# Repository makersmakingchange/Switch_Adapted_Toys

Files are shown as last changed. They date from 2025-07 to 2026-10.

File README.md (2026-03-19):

# Switch Adapted Toys
Welcome to the Maker's Making Change resources for Switch Adapted Toys.

This repository is a collection of guides, files, and tools to help individuals and organizations modify toys for use with assistive switches. These adaptations make play more inclusive for children and adults with limited mobility, giving them the power to activate toys with the press of a button—on their own terms.

## What You'll Find Here
 - How-To Guides: - Step-by-step instructions for adapting toys with simple tools and materials and an easy-to-use template for writing toy instructions
 - Educational Resources: Information on how to switch adapt a new toy
 - Equipment lists: Complete list of adapted toys and the tools and components needed to adapt them
 <!-- - Workshop Materials: Handouts and presentation slides for toy hackathons and build nights -->

<!--
## Who This Is For
 - Makers and volunteers interested in assistive technology
 - Therapists and educators supporting play-based learning
 - Families looking to adapt toys at home
 - Nonprofits and schools running toy adaptation workshops
-->

## How To Find a Toy
Toys have been organized by type into separate folders inside the "Toy_Instructions" folder. We have organized the toys this way to help make it easier to find a suitable substitution if you are unable to get the toy someone has requested directly.

You can search for a specific toy by typing in the search field on the repository.

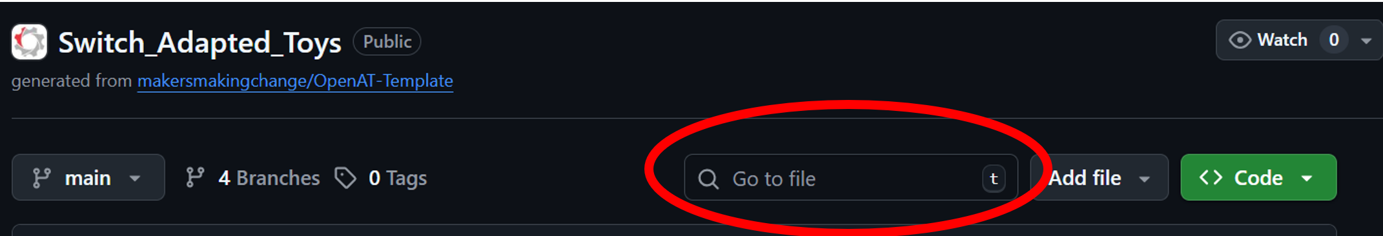
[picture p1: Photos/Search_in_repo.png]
Screenshot of the top of the GitHub repository with the search field circled in red.


The search is very broad, and does not rely on exact  matching between the files/folder you're looking for and what you type. For example, if you type "Rachel", the search will find the Switch Adapted Ms. Rachel Speak and Sing Doll, but also any instances where those letters appear in that order, regardless of what charaters are between them.

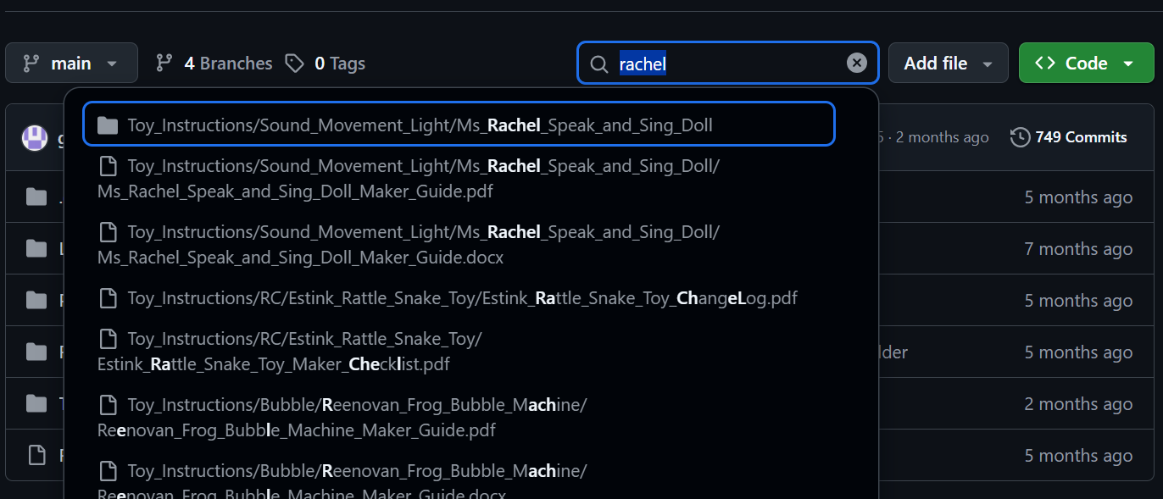
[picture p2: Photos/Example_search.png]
Screenshot of the search results when someone types "Rachel" into the search field.


## Accessing Files

Once you have found the files you need, you can download them from GitHub. You can download individual files by clicking on the down arrow on the page. 

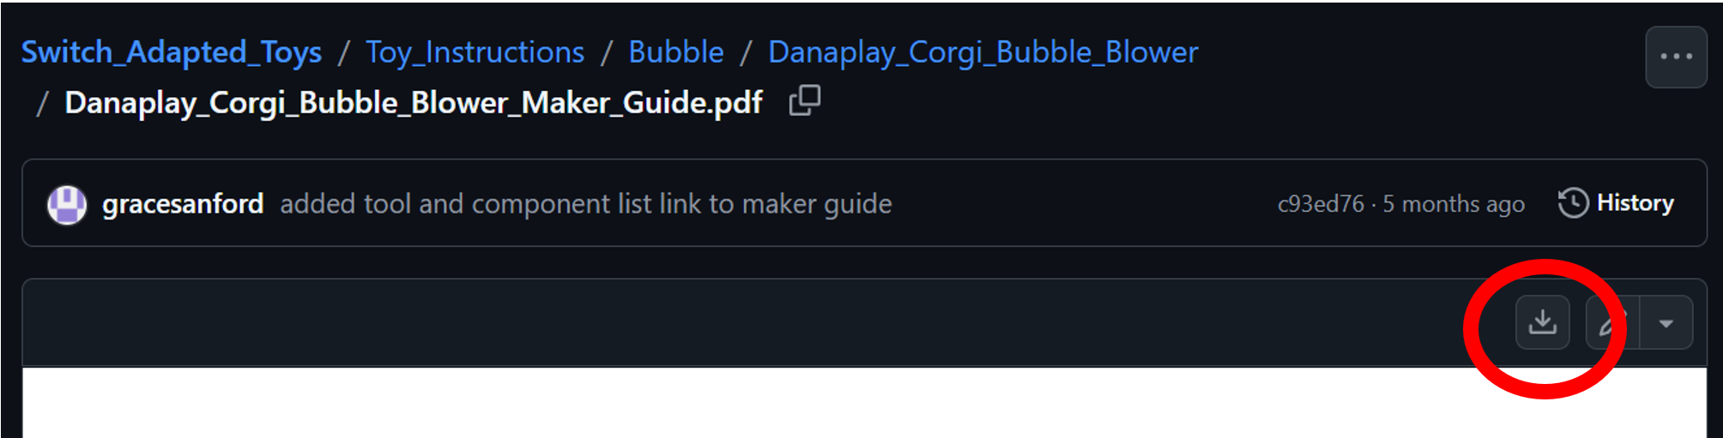
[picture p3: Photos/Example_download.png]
Screenshot highlighting the download button on GitHub.


You will need to download documents (PDFs or Word documents) to be able to access any hyperlinks in those documents.

Some document types, such as Word documents, do not display on the GitHub webpage, and you will have to download them to view. Clicking the "View raw" button will display the files on your web browser (if possible), or download them to your computer.

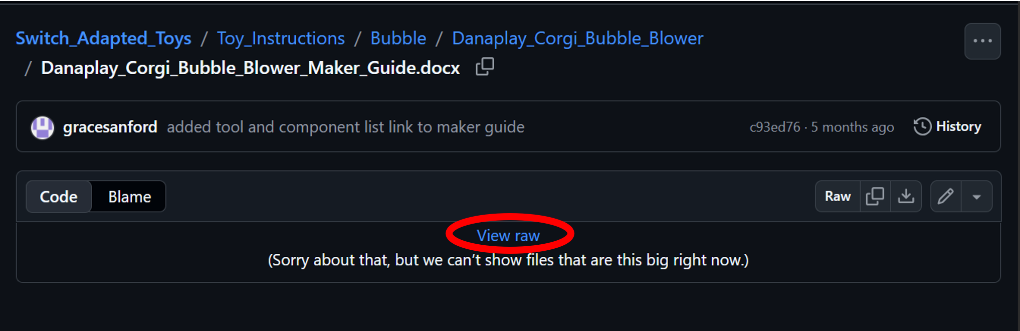
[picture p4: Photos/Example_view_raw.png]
Screenshot highlighting the View raw option for a file type that doesn't preview on GitHub.


## Get Involved
This repository is open source and community-driven. Feel free to open issues, suggest improvements, or submit pull requests! Whether you're documenting your own process or translating guides into another language, your contributions help make inclusive play more accessible for everyone.

## License
All content is shared under the [Creative Commons Attribution-ShareAlike 4.0 License (CC BY-SA 4.0)](https://creativecommons.org/licenses/by-sa/4.0/), unless otherwise noted.

<!-- ABOUT MMC START -->
## About Makers Making Change
[Makers Making Change Logo](https://www.makersmakingchange.com/)

Makers Making Change is a program of [Neil Squire](https://www.neilsquire.ca/), a Canadian non-profit that uses technology, knowledge, and passion to empower people with disabilities.

Makers Making Change leverages the capacity of community based Makers, Disability Professionals and Volunteers to develop and deliver affordable Open Source Assistive Technologies.

 - Website: [www.MakersMakingChange.com](https://www.makersmakingchange.com/)
 - GitHub: [makersmakingchange](https://github.com/makersmakingchange)
 - Bluesky: [@makersmakingchange.bsky.social](https://bsky.app/profile/makersmakingchange.bsky.social)
 - Instagram: [@makersmakingchange](https://www.instagram.com/makersmakingchange)
 - Facebook: [makersmakechange](https://www.facebook.com/makersmakechange)
 - LinkedIn: [Neil Squire Society](https://www.linkedin.com/company/neil-squire-society/)
 - Thingiverse: [makersmakingchange](https://www.thingiverse.com/makersmakingchange/about)
 - Printables: [MakersMakingChange](https://www.printables.com/@MakersMakingChange)

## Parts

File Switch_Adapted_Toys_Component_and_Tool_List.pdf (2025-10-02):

V1.0 | September 2025

## Switch Adapted Toys COMPONENT AND TOOL LIST

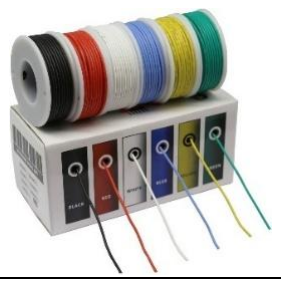
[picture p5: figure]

©2025 Neil Squire Society.

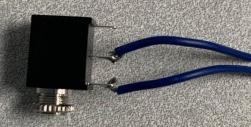
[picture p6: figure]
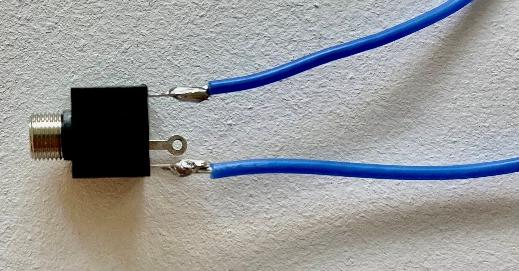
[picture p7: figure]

This work is licensed under the CC BY SA 4.0 License: http://creativecommons.org/licenses/by-sa/4.0
Files available at makersmakingchange/Switch_Adapted_Toys: Resources and instructions for switch adapting toys (https://github.com/makersmakingchange/Switch_Adapted_Toys) Page 1 of 7

This is a list of commonly used components and tools that are used to switch adapt toys. Most items on this list can be purchased from different manufacturers for various prices. The tools are widely used and can be purchased from most local hardware stores. Note that not every tool and component listed is needed to adapt each toy, refer to the first page of the toy’s Maker Guide for more information.

## Components

Device Type | Component | Purchase Link | Notes
| 3.5 mm Rectangular Mono Jack | DigiKey Link (https://www.digikey.ca/en/products/detail/cui-inc/MJ-3502/281321) | Most used Mono Jack. Solder wires onto the two tabs closest to the cable input.
| 3.5 mm Square Mono Jack | DigiKey Link (https://www.digikey.ca/en/products/detail/schurter-inc/4832-2211/2646631) | Solder wires onto the two tabs directly across from each other.
| 22 AWG Wire | Amazon Link (https://a.co/d/4Lc9GPb) | Any 22 AWG silicone wire will work.

Mono Jack

## Switch Adapted Toys COMPONENT AND TOOL LIST

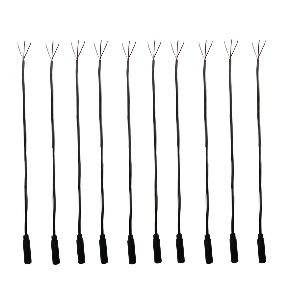
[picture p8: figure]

©2025 Neil Squire Society.

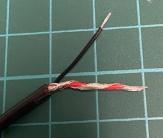
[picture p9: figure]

Files available at makersmakingchange/Switch_Adapted_Toys: Resources and instructions for switch adapting toys (https://github.com/makersmakingchange/Switch_Adapted_Toys) Page 2 of 7

Cables

3.5 mm F/Bare Mono Cable (1 ft) | Amazon Link (https://www.amazon.ca/dp/B082VW97TT?ref=fed_asin_title) | 10 / $20.22.
3.5 mm F/Bare Stereo Cable (1ft) | Amazon Link (https://www.amazon.ca/dp/B0F3791KNY?ref=fed_asin_title&th=1) | To use as a mono cable: Fully strip the insulation off the white wire and 0.5 cm from the red and black wires. Wrap the exposed wire around the red cable. 10 / $10.99
Flex PCB | Request from MMC (https://www.makersmakingchange.com/product/battery-interrupter-flex-pcb/01tJR000000694IYAQ) | -
3.5 mm Mono Jack Flat Rectangular | Digikey Link (https://www.digikey.ca/en/products/detail/cui-devices/SJ1-3513/738683) | Flex PCB is soldered onto the mono jack.

Battery
Interrupter

## Switch Adapted Toys COMPONENT AND TOOL LIST

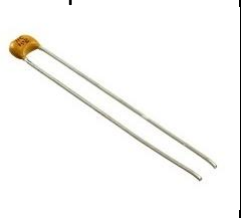
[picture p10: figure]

©2025 Neil Squire Society.

Files available at makersmakingchange/Switch_Adapted_Toys: Resources and instructions for switch adapting toys (https://github.com/makersmakingchange/Switch_Adapted_Toys) Page 3 of 7

Additional
Components

10,000 pf (103)
Capacitor

Digikey Link (https://www.digikey.ca/en/products/detail/vishay-beyschlag-draloric-bc-components/K103K15X7RH5TL2/286565)

Used for adapting multiple RC cars. Amazon Dinosaur RC Car (https://github.com/makersmakingchange/Switch_Adapted_Toys/tree/main/Toy_Instructions/Available/RC/Amazon_Dinosaur_RC_Car)

Prextex RC Race and Police Car (https://github.com/makersmakingchange/Switch_Adapted_Toys/tree/main/Toy_Instructions/Available/RC/Pretex_RC_Race_and_Police_Car)

Prextex RC Truck and Tractor (https://github.com/makersmakingchange/Switch_Adapted_Toys/tree/main/Toy_Instructions/Available/RC/Pretex_RC_Truck_and_Tractor)

Toggle Switch | Amazon Link (https://a.co/d/6loZYGi) | Used in Nerf N-strike Elite Hyperfire Blaster. (https://github.com/makersmakingchange/Switch_Adapted_Toys/tree/main/Toy_Instructions/Available/Water_Nerf_Gun/Nerf_Nerf-N-Strike_Elite_HyperFire_Blaster) 10/$15.98.

## Switch Adapted Toys COMPONENT AND TOOL LIST

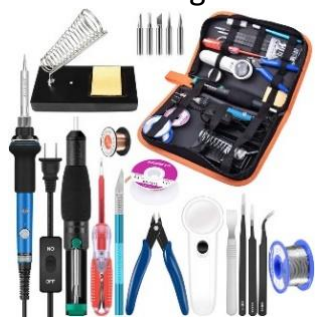
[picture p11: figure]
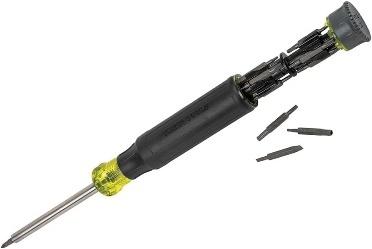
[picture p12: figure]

©2025 Neil Squire Society.

Files available at makersmakingchange/Switch_Adapted_Toys: Resources and instructions for switch adapting toys (https://github.com/makersmakingchange/Switch_Adapted_Toys) Page 4 of 7

## Tools

Tool | Purchase Link | Price ($ CAD) | Notes
Soldering Kit | Amazon Link (https://a.co/d/g95ULy8) | 39.99 | Easy and cheap way to acquire a lot of tools. Includes: Soldering iron, solder, soldering iron stand, sponge, Phillips and flathead screwdriver, flush cutter, tweezers, etc.
Wire Strippers | Amazon Link (https://www.amazon.ca/Professional-crimping-Multi-Tool-Stripper-Multi-Function/dp/B073YG65N2?s=hi) | 21.43 | Required for mono jack / cable toys.
Multi Head Screwdriver | Amazon Link (https://www.amazon.ca/Multi-Bit-Precision-Screwdriver-Tamperproof/dp/B09SVP9NDQ) | 31.77 | Comes with 26 bits. Helpful to have a few more screwdrivers than soldering irons for events. Most toys use Phillips Screwdrivers.
Cable Tie | Amazon Link (https://www.amazon.ca/Cable-Self-Locking-Straps-Durable-Auto-Locking/dp/B0BL6JSMRM) | 10.99 | Attach to mono cable on inside of toy for strain relief. Pack of 150 cable ties: 50 - 10cm 50 - 20cm 50 - 30cm

## Switch Adapted Toys COMPONENT AND TOOL LIST


©2025 Neil Squire Society.

Files available at makersmakingchange/Switch_Adapted_Toys: Resources and instructions for switch adapting toys (https://github.com/makersmakingchange/Switch_Adapted_Toys) | Page 5 of 7
Flush Cutter | - | - | Used to cut wires. *Included in soldering kit*
Drill and Drill Bits | Amazon Link (https://a.co/d/0jTuJfl) | 69.99 | Needed to create hole in hardshell toys for cable/jack. 1/8" drill bit for mono cable, 1/4" drill bit for mono jack.
Safety Glasses | Amazon Link (https://www.amazon.ca/Anti-Scratch-Protective-Resistant-Construction-Laboratory/dp/B0C7ZQKL92?s=hi&sp_csd=d2lkZ2V0TmFtZT1zcF9hdGY) | 39.50 | Pack of 28.
Silicone Mat | Canadian Tire Link (https://www.canadiantire.ca/en/pdp/master-chef-silicone-non-stick-baking-sheet-red-15-x-11-in-0420900p.html?rq=master+chef+silicone+baking+sheet) | 9.99 | Often goes on sale for $5. Useful to have one with each soldering iron at events.
Silicone Mat | Amazon Link (https://www.amazon.ca/dp/B088M3JCP2?s=hi&sp_csd=d2lkZ2V0TmFtZT1zcF9kZXRhaWw) | 25.99 | Good for a personal workstation.

## Switch Adapted Toys COMPONENT AND TOOL LIST


©2025 Neil Squire Society.

Files available at makersmakingchange/Switch_Adapted_Toys: Resources and instructions for switch adapting toys (https://github.com/makersmakingchange/Switch_Adapted_Toys) | Page 6 of 7
Pliers | Amazon Link (https://a.co/d/5ah4y0g) | 11.99 | -
Long Nose Pliers | Amazon Link (https://a.co/d/dbGVOhI) | 11.99 | -
Multimeter | Amazon Link (https://a.co/d/5vZuu9m) | 23.99 | Useful for deciding where to solder new wires onto a PCB.
Electrical Tape | Amazon Link (https://a.co/d/cVN6GOs) | 4.70 | Often required for toys adapted with a mono jack.

## Switch Adapted Toys COMPONENT AND TOOL LIST


©2025 Neil Squire Society.

Files available at makersmakingchange/Switch_Adapted_Toys: Resources and instructions for switch adapting toys (https://github.com/makersmakingchange/Switch_Adapted_Toys) | Page 7 of 7
Helping Hands | Amazon Link (https://www.amazon.ca/dp/B0CZLQGM2Z?ref=fed_asin_title) | 29.99 | Can be helpful when soldering.
Hot Glue Gun | Amazon Link (https://www.amazon.ca/SOJITAS-Extra-Long-Heating-Precision-Support/dp/B0852YJJSP?sp_csd=d2lkZ2V0TmFtZT1zcF9hdGY) | 19.99 | -
Needle and Thread | - - | | Sometimes needed to close plush toys.

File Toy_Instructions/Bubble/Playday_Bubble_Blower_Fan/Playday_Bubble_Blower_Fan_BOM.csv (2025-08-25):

 | Device: Bubble Blower Fan |  |  | Total Cost | Total Print time (hr) | Total filament (g)
 | Version: V1.0 | Date Created: 2022-Aug-02 |  | $5.74 | 0.00 | 0
 | Commercial Parts
ID | Description | P/N | Supplier | Quantity Needed | Pkg Quantity | Price per package | Price per Unit | Price for qty needed | Link
1 | Play Day Bubble Blower Fan |  | Walmart | 1 | 1 | $4.48 | $4.48 | $4.48 | https://www.walmart.com/ip/Play-Day-Bubble-Blower-Fan-Blue-Battery-Operated-Bubble-Maker/453931321
2 | Jack, Mono, 3.5 mm | MJ-3507 | Digikey | 1 | 1 | $1.26 | $1.26 | $1.26 | https://www.digikey.ca/en/products/detail/cui-devices/MJ-3507/2160900
3 | Wire, 8 cm | n/a |  | 2 | 1 |  | $- | $-
 | 3D Printed Parts ESTIMATED PRICING USING 1KG ROLL COST: | $25.00
 | Part | Description |  | Quantity Needed | TOTAL Mass (g) | Estimated Price | Print Time (Min) | Link
 | n/a |  |  |  |  | $-
 |  |  |  |  | Total Print Cost: | $-
 | Tools for Assembly
 | Screwdriver, Phillips, Small
 | Soldering Iron
 | Solder sucker OR De-solder tape
 | Hot Glue gun
 | Alternatives (if there are other sources for some parts link them below)
 | Part and description | Link

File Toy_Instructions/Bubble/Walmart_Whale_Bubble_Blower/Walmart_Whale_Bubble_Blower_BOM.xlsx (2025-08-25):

Device: Switch Adapted Whale Bubble Blower |  | Total Cost | Total Print time (hr) | Total filament (g)
Version: V1.0 | Date Created: 20/12/2022 | $27.53 | 0.00 | 0
Commercial Parts:
Part type (Electrical. Mechanical, Sanitization, ect) | Part Name | Quantity Needed | Pkg Quantity | Price per package | Price per Unit | Price for qty needed | Link
Toy | Balnore Bubble Machine | 1 | 1 | $25.00 | $25.00 | $25.00 | https://www.amazon.ca/Balnore-Machine-Automatic-Parties-Wedding/dp/B07MW21SJ6?hvadid=335949156370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
Electrical | 3.5mm mono jack | 1 | 1 | $2.53 | $2.53 | $2.53 | https://www.digikey.ca/en/products/detail/switchcraft-inc/35RAPC2AV/772080
3D Printed Parts ESTIMATED PRICING USING 1KG ROLL COST: | $25.00
Part | Description | Quantity Needed | TOTAL Mass (g) | Estimated Price | Print Time (Min) | Link
 |  |  |  | $0.00
 |  |  |  | $0.00
 |  |  |  | $0.00
 |  |  |  | $0.00
 |  |  |  | $0.00
 |  |  | Total Print Cost: | $0.00
Tools for Assembly
Drill with 1/4" drill bit
Soldering iron and solder
Phillips head screwdriver (included with toy)
Wire cutters
Wire strippers
Ruler
Alternatives (if there are other sources for some parts link them below)
Part and description | Link
Balnore Bubble Machine | https://www.fruugo.ca/balnore-bubble-machine-with-concentrated-bubble-solution/p-110751399-233776256?language=en&ac=google&asc=pmax
Balnore Bubble Machine | https://toptoyusa.com/product/balnore-bubble-machineautomatic-bubble-maker-2000-bubble-blower-for-kidseasy-to-use-for-parties-wedding-baby-showers-indoor-outd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

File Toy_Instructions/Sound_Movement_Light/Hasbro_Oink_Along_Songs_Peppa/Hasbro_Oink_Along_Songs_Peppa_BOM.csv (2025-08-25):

Switch Adapted Peppa Pig |  |  |  |  |  |  |  | Unit Cost | Total Cost | Total Print time (hr) | Total filament (g)
Version: V1.0 |  | Last Updated: 2022-Nov-28 |  |  |  |  |  | $27.72 | $37.18 | 0.00 | 0
Commercial Parts
ID | Part Name | Part Type | QTY | QTY/PKG | $/PKG | PKG QTY | $/Unit | Extended | Total | Link
 | Peppa Pig Oink-Along Songs Singing Plush Doll | Toy | 1 | 1 | $24.94 | 1 | $24.94 | $24.94 | $24.94 | https://a.co/d/gVYby6S
 | 3.5mm Female Plug to Bare Wire Cable | Electrical | 1 | 4 | $10.99 | 1 | $2.75 | $2.75 | $10.99 | https://a.co/d/bglRpvv
 | Small Cable Tie/Zip Tie (15 cm works well) | Mechanical | 1 | 40 | $1.25 | 1 | $0.03 | $0.03 | $1.25 | Local dollar store
 |  |  |  |  |  | 0 | $- | $- | $-
 |  |  |  |  |  | 0 | $- | $- | $-
 |  |  |  |  |  | 0 | $- | $- | $-
 |  |  |  |  |  | 0 | $- | $- | $-
3D Printed Parts ESTIMATED PRICING USING 1KG ROLL COST: |  | $25.00
ID | Part | Material | QTY | Mass (g) / Unit | Time / Unit |  | Print Time (Min) | Estimated Price |  | Link
 |  |  |  |  |  |  |  | $-
 |  |  |  |  |  |  |  | $-
 |  |  |  |  |  |  |  | $-
 |  |  |  |  |  |  |  | $-
 |  |  |  |  |  |  |  | $-
 |  |  |  |  |  |  |  | $-
Custom Printed Circuit Board (PCB)
ID | Part |  | QTY
Tools for Assembly
 | Small Philips or flathead screwdriver
 | Drill with 1/8" drill bit
 | Flush cutters
 | Wire strippers
 | Soldering iron and solder
Alternatives (if there are other sources for some parts link them below)
ID | Part and description |  |  |  |  |  |  |  |  | Link
 | Peppa Pig Oink-Along Songs Singing Plush Doll | https://www.walmart.ca/en/ip/peppa-pig-oink-along-songs-singing-plush-doll-with-sparkly-red-dress-and-bow-english-multi/6000203116305?rrid=richrelevance
 | Peppa Pig Oink-Along Songs Singing Plush Doll | https://www.toysrus.ca/en/Peppa-Pig-Oink-Along-Songs-Peppa-Singing-Plush-Doll-with-Sparkly-Red-Dress-and-Bow--Sings-3-Songs---English-Edition/C442196D.html
 | Cable ties | https://www.walmart.ca/en/ip/stanley-8-cable-ties-black/6000197428790

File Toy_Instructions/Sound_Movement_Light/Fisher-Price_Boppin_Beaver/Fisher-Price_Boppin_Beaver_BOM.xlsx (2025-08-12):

Boppin' Beaver |  | Total Cost | Total Print time (hr) | Total filament (g)
Version: V1.0 | Date Created: 4/20/2021 | $12.13 | 0.00 | 0
Commercial Parts:
Part type (Electrical. Mechanical, Sanitization, ect) | Manufacturer Part Number | Quantity Needed | Pkg Quantity | Price per package | Price per Unit | Price for qty needed | Link
Boppin' Beaver Linkimal Toy | GTJ74 | 1 | 1 | $9.99 | $9.99 | $9.99 | https://www.walmart.com/ip/Fisher-Price-Linkimals-Boppin-Beaver-Musical-Baby-Toy/241124540?athbdg=L1300
3.5 mm Mono Jack | CP-3502MJ-ND | 1 | 1 | $2.14 | $2.14 | $2.14 | https://www.digikey.ca/short/pq1d1z
3D Printed Parts ESTIMATED PRICING USING 1KG ROLL COST: | $25.00
Part | Description | Quantity Needed | TOTAL Mass (g) | Estimated Price | Print Time (Min) | Link
 |  |  |  | $0.00
 |  |  |  | $0.00
 |  |  |  | $0.00
 |  |  |  | $0.00
 |  |  |  | $0.00
 |  |  | Total Print Cost: | $0.00
Tools for Assembly
Drill with 1/4" drill bit
Wire strippers
Flush Cutters
Phillips Screwdriver
Soldering Iron
Solder
Ruler
Alternatives (if there are other sources for some parts link them below)
Part and description | Link
3.5mm Female Stero Cable - 6ft | 3.5mm Stereo Plug/Jack M/F Extension Cable - 6ft - PrimeCables® (https://www.primecables.ca/p-306304-cab-audio-ex-mf-6ft-35mm-stereo-plugjack-mf-extension-cable-6ft-primecables)
3.5mm Female Stero Cable - 6ft For US SHIPPING | https://www.allelectronics.com/item/cb-333/6-3.5mm-m-f-extension-cord/1.html
 | Can also sometimes be sourced from dollar store

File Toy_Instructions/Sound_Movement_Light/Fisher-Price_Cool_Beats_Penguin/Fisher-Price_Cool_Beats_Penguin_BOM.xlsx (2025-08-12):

Penguin Switch Adapted Toy |  | Total Cost | Total Print time (hr) | Total filament (g)
Version: V1.0 | Date Created: JUNE 2022 | $43.28 | 0.00 | 0
Commercial Parts:
Part type (Electrical. Mechanical, Sanitization, ect) | Manufacturer Part Number | Quantity Needed | Pkg Quantity | Price per package | Price per Unit | Price for qty needed | Link
Cool Beats Penguin | GXX17 | 1 | 1 | $39.00 | $39.00 | $39.00 | Fisher-Price Linkimals Cool Beats Penguin, Musical Infant Toy with Lights, Motions, and Educational Songs for Infants and Toddlers, Multicolor : Amazon.ca: Toys & Games (https://www.amazon.ca/Fisher-Price-Linkimals-Penguin-Educational-Toddlers/dp/B08V77S98Q)
2x 3.5 mm Mono Jack | CP-3502MJ-ND | 2 | 1 | $2.14 | $2.14 | $4.28 | https://www.digikey.ca/short/pq1d1z
3D Printed Parts ESTIMATED PRICING USING 1KG ROLL COST: | $25.00
Part | Description | Quantity Needed | TOTAL Mass (g) | Estimated Price | Print Time (Min) | Link
N/A |  |  |  | $0.00
 |  |  |  | $0.00
 |  |  |  | $0.00
 |  |  |  | $0.00
 |  |  |  | $0.00
 |  |  | Total Print Cost: | $0.00
Tools for Assembly
Drill with 1/4" drill bit
Wire Strippers
Flush cutters
Phillips screwdriver
Soldering Iron
Solder
Ruler
Alternatives (if there are other sources for some parts link them below)
Part and description | Link

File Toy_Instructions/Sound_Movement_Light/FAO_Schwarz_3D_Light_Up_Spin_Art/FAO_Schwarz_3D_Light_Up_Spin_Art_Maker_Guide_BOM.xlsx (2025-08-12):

Device: Spin Art Switch Adapted Toy |  | Total Cost | Total Print time (hr) | Total filament (g)
Version: V1.0 | Date Created: 7/19/2021 | $32.04 | 0.00 | 0
Commercial Parts:
Part type (Electrical. Mechanical, Sanitization, ect) | Part Name | Quantity Needed | Pkg Quantity | Price per package | Price per Unit | Price for qty needed | Link
Electrical | Mono jack (MJ-3502) (digikey:CP-3502MJ-ND) | 3 | 10 | $19.42 | $1.94 | $5.83 | https://www.digikey.ca/short/pq1d1z
Electrical | 22 AWG wire (quantity in m) | 0.5 | 45 | $22.55 | $0.50 | $0.25 | https://www.digikey.ca/en/products/detail/sparkfun-electronics/PRT-11375/5956252
Toy | Spin Art Toy | 1 | 1 | $25.96 | $25.96 | $25.96 | https://www.thebay.com/product/fao-schwarz-led-spin-art-set-90285654.html
3D Printed Parts ESTIMATED PRICING USING 1KG ROLL COST: | $25.00
Part | Description | Quantity Needed | TOTAL Mass (g) | Estimated Price | Print Time (Min) | Link
 |  |  |  | $0.00
 |  |  | Total Print Cost: | $0.00
Tools for Assembly
Wire strippers
Flush cutters
Screw driver
Drill
Drill bit (1/4")
Soldering Iron
Solder
Permanent marker
Ruler
Alternatives (if there are other sources for some parts link them below)
Part and description | Link
Alternate Toy | https://www.amazon.ca/dp/B07ML4D9LZ/

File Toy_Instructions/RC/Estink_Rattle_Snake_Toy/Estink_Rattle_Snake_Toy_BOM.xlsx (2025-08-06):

Slithering Snake |  | Total Cost | Total Print time (hr) | Total filament (g)
Version: V1.0 | Date Created: 25/06/2021 | $36.68 | 1.40 | 7.877
Commercial Parts:
Part type (Electrical. Mechanical, Sanitization, ect) | Part Name | Quantity Needed | Pkg Quantity | Price per package | Price per Unit | Price for qty needed | Link
Electrical | Mono jack (MJ-3502) (digikey:CP-3502MJ-ND) | 3 | 10 | $19.42 | $1.94 | $5.83 | https://www.digikey.ca/short/pq1d1z
Electrical | 22 AWG wire (quantity in m) | 1 | 45 | $22.55 | $0.50 | $0.50 | https://www.digikey.ca/en/products/detail/sparkfun-electronics/PRT-11375/5956252
Mechanical | Heat shrink wire wrap | 2 | 270 | $15.99 | $0.06 | $0.12 | https://www.amazon.ca/Moveland-270PCS-Adhesive-Assortment-Electrical/dp/B07N2M4345
Mechanical | #4 metal screw, 3/8" length (mcmaster: 90190A108) | 2 | 100 | $2.52 | $0.03 | $0.05 | https://www.mcmaster.com/90190A108/
Toy | Slithering Snake Toy | 1 | 1 | $29.99 | $29.99 | $29.99 | https://www.mastermindtoys.com/products/black-remote-controlled-snake
3D Printed Parts ESTIMATED PRICING USING 1KG ROLL COST: | $25.00
Part | Description | Quantity Needed | TOTAL Mass (g) | Estimated Price | Print Time (Min) | Link
Mono Jack Box |  | 1 | 4.949 | $0.12 | 68
Mono Jack Box Lid |  | 1 | 2.928 | $0.07 | 16
 |  |  | Total Print Cost: | $0.20
Tools for Assembly
Wire strippers
Flush cutters
Screw driver
Drill
Drill bit (5/32")
Soldering Iron
Solder
Permanent marker
Ruler
Needle Nosed Pliers (optional but helpful)
Alternatives (if there are other sources for some parts link them below)
Part and description | Link
Alternative for screws, #4 metal screw, 3/8" length (amazon) | https://www.amazon.ca/gp/product/B00GI86MW8
Alternative toy, remote control centipede | https://www.mastermindtoys.com/products/remote-control-centipede

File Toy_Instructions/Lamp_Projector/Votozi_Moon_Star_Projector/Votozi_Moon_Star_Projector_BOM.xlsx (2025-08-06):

Device: Star Master Projector Toy |  | Total Cost | Total Print time (hr) | Total filament (g)
Version: V1.0 | Date Created: 4/20/2021 | $26.31 | 0.00 | 0
Commercial Parts:
Part type (Electrical. Mechanical, Sanitization, ect) | Part Name | Quantity Needed | Pkg Quantity | Price per package | Price per Unit | Price for qty needed | Link
Electrical | Mono jack (MJ-3502) (digikey:CP-3502MJ-ND) | 3 | 10 | $19.42 | $1.94 | $5.83 | https://www.digikey.ca/short/pq1d1z
Electrical | 22 AWG wire (quantity in m) | 1 | 45 | $22.55 | $0.50 | $0.50 | https://www.digikey.ca/en/products/detail/sparkfun-electronics/PRT-11375/5956252
Toy | Star Master Projector Toy | 1 | 1 | $19.98 | $19.98 | $19.98 | https://www.amazon.ca/dp/B07X5JZTBF/
3D Printed Parts ESTIMATED PRICING USING 1KG ROLL COST: | $25.00
Part | Description | Quantity Needed | TOTAL Mass (g) | Estimated Price | Print Time (Min) | Link
 |  |  |  | $0.00
 |  |  | Total Print Cost: | $0.00
Tools for Assembly
· Drill
· Wire strippers
· Solder
· Soldering iron
· ¼” Drill bit
· Philips head screwdriver
· Flush cutters
· Craft knife
· Permanent marker
Alternatives (if there are other sources for some parts link them below)
Part and description | Link
Alternative Seller of Toy | https://www.amazon.ca/dp/B07CQC1MQF/

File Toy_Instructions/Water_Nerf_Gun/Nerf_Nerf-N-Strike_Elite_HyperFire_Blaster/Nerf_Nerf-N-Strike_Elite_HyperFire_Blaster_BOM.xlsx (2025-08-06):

Device: Switch Adapted Nerf Gun |  | Total Cost | Total Print time (hr) | Total filament (g)
Version: V1.0 | Date Created: 01/06/2023 | $91.19 | 8.63 | 64
Commercial Parts:
Part type (Electrical. Mechanical, Sanitization, ect) | Part Name | Quantity Needed | Pkg Quantity | Price per package | Price per Unit | Price for qty needed | Link
Mechanical | Nerf N-Strike Elite HyperFire Blaseter | 1 | 1 | $71.99 | $71.99 | $71.99 | https://www.amazon.ca/dp/B018KLHT5O
Electrical | D Cell Battery | 4 | 4 | $12.82 | $3.21 | $12.82 | https://www.amazon.ca/dp/B00000JHQC/
Mechanical | 1/4-20 T Nut | 3 | 100 | $14.40 | $0.14 | $0.43 | https://www.mcmaster.com/90975A309/
Mechanical | 1/4-20 Bolt | 2 | 25 | $17.99 | $0.72 | $1.44 | https://www.amazon.ca/dp/B097NWWQFC/
Electrical | Toggle Switch | 1 | 10 | $15.96 | $1.60 | $1.60 | https://www.amazon.ca/dp/B01BWL7Z44/ | https://www.aliexpress.com/item/1005001558947112.html
Electrical | Mono Jack | 1 | 10 | $13.09 | $1.31 | $1.31 | https://www.amazon.ca/dp/B07R9SV6F5/
3D Printed Parts ESTIMATED PRICING USING 1KG ROLL COST: | $25.00
Part | Description | Quantity Needed | TOTAL Mass (g) | Estimated Price | Print Time (Min) | Link
Desk Stand | Allows the gun to stand unsupported on a surface | 1 | 27 | $0.68 | 232
Bolt Stand | Allows the gun to be attacked to a 1/4-20 system | 1 | 37 | $0.92 | 286
 |  |  |  | $0.00
 |  |  |  | $0.00
 |  |  |  | $0.00
 |  |  | Total Print Cost: | $1.60
Tools for Assembly
Alternatives (if there are other sources for some parts link them below)
Part and description | Link

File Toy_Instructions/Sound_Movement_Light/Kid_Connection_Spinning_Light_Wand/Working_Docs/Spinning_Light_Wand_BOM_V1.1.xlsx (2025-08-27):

 | Spinning Light Wand Adaptation |  | Total Cost | Total Print time (hr) | Total filament (g)
 | Version: V1.1 (V1.0 BOM found below) | June, 2022 | $9.12 | 2.58 | 37
ID | Commercial Parts
 |  | Model | QTY | Pkg Quantity | Price per package | Price per Unit | Price for qty needed | Link
1 | Spinning Light Wand Toy | SKU 6000201173988 | 1 | 1 | $5.00 | $5.00 | $5.00 | https://www.walmart.ca/en/ip/spinning-light-wand-yellowblue/6000201173987
2 | 3.5 mm Mono Jack | Shurter 4832.2211 | 1 | 1 | $2.02 | $2.02 | $2.02 | https://www.digikey.ca/en/products/detail/schurter-inc/4832-2211/2646631
3 | #4 1/2" screws | 9018940 | 8 | 75 | $8.22 | $0.11 | $0.88 | https://www.amazon.ca/Prime-Line-9018940-Self-Tapping-Phillips-Plated/dp/B074ZXK788?rnid=12035759011
4 | Non-slip circles |  | 4 | 20 | $1.50 | $0.07 | $0.30 | Bought at dollarama
 | 3D Printed Parts ESTIMATED PRICING USING 1 KG ROLL COST: | $25.00
 | Part |  | QTY | TOTAL Mass (g) | Estimated Price | Print Time (Min) | Link
5 | Base | Base.stl | 1 | 29 | $0.73 | 112
6 | Jack Cover | Jack_Cover.stl | 1 | 8 | $0.20 | 43
 |  |  |  | Total Print Cost: | $0.93
 | Tools for Assembly
 | #0 Phillips Screwdriver
 | #0 Robertson Screwdriver (depending on which screws you get)
 | Soldering Iron
 | Hot glue gun
 | Alternatives (if there are other sources for some parts link them below)
 | Part and description | Link
 | 3.5 mm Mono Jack | https://www.digikey.ca/en/products/detail/cui-devices/SJ1-3513/738683
 | Can likely buy screws in smaller quanities at local hardware store. They typically have a #0 Robertson head
 |  |  | Total Cost | Total Print time (hr) | Total filament (g)
 | Version: V1.0 |  | $9.73 | 6.13 | 62
 | Commercial Parts
 |  | Model | QTY | Pkg Quantity | Price per package | Price per Unit | Price for qty needed | Link
 | Spinning Light Wand Toy | SKU 6000201173988 | 1 | 1 | $5.00 | $5.00 | $5.00 | https://www.walmart.ca/en/ip/spinning-light-wand-yellowblue/6000201173987
 | 3.5 mm Mono Jack | Shurter 4832.2211 | 1 | 1 | $2.02 | $2.02 | $2.02 | https://www.digikey.ca/en/products/detail/schurter-inc/4832-2211/2646631
 | 1/2" Hex Nuts |  | 2 | 1 | $0.58 | $0.58 | $1.16 | https://www.homedepot.ca/product/paulin-1-2-13-inch-finished-hex-nut-zinc-plated-grade-5-unc/1000123718
 | 3D Printed Parts ESTIMATED PRICING USING 1 KG ROLL COST: | $25.00
 | Part |  | QTY | TOTAL Mass (g) | Estimated Price | Print Time (Min) | Link
 | Base | Base.stl | 1 | 53 | $1.32 | 320
 | Base Bottom Cover | Base_Bottom_Cover.stl | 1 | 9 | $0.22 | 48
 |  |  |  | Total Print Cost: | $1.55
 | Tools for Assembly
 | #0 Phillips Screwdriver
 | Flat head screw driver
 | Soldering Iron
 | Hot glue gun
 | Super Glue
 | Alternatives (if there are other sources for some parts link them below)
 | Part and description | Link
 | 3.5 mm Mono Jack | https://www.digikey.ca/en/products/detail/cui-devices/SJ1-3513/738683

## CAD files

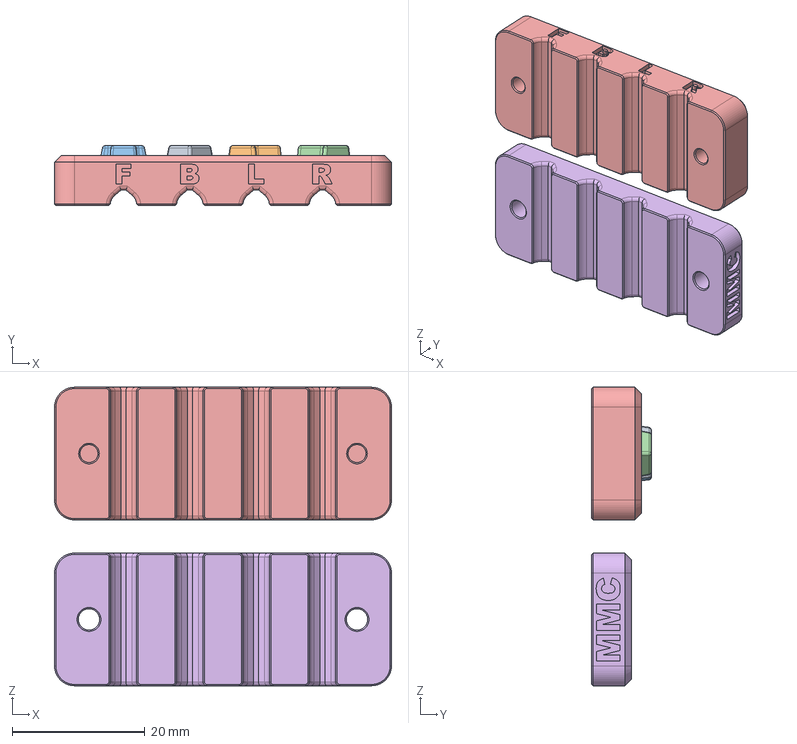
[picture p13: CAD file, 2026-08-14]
Resources/Cable_Clamp/Cable_Clamp_FBLR.step
50.8 x 9.00 x 45.0 mm
Cable_Clamp_Top_FBLR (1)
Cable_Clamp_Top_FBLR (2)
Cable_Clamp_Top_FBLR (4)
Cable_Clamp_Top_FBLR (3)
Cable_Clamp_Bottom

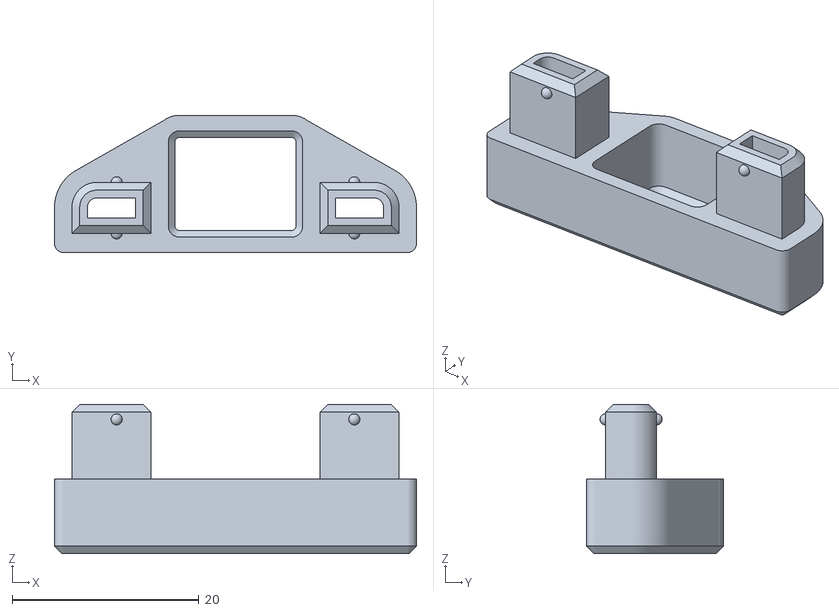
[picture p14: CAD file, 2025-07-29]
Toy_Instructions/Bubble/Playday_Light_Up_Bubble_Blaster/Battery_Interrupter_Maker_Guide/3D_Printing_Files/Cable_Tie_Holder_Back.stl
38.8 x 14.7 x 16.0

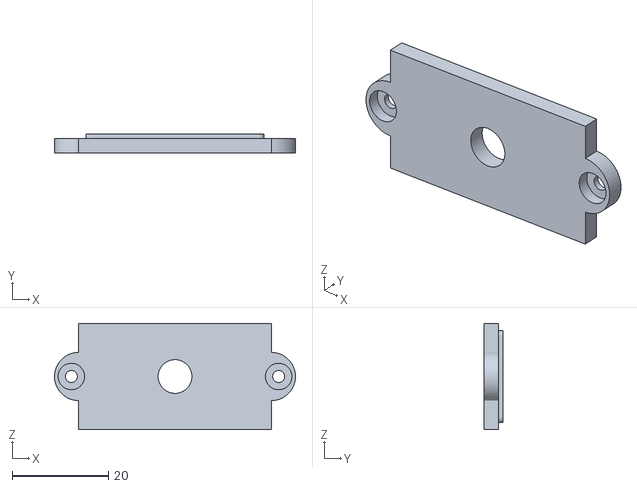
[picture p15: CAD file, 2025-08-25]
Toy_Instructions/RC/Estink_Rattle_Snake_Toy/3D_Printing_Files/monojackboxlid.stl
50.0 x 4.00 x 22.0

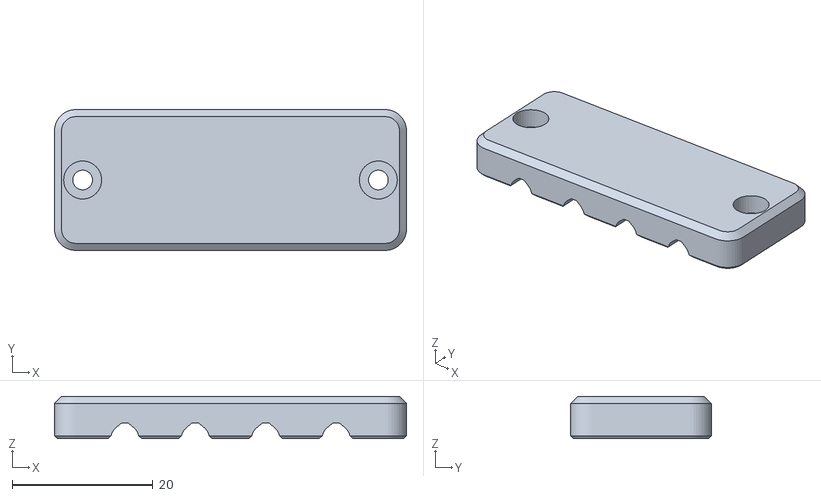
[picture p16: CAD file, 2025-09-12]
Toy_Instructions/RC/Monster_Jam_RC_Cars_Various/3D_Printing_Files/Cable_Clamp_Back.stl
50.0 x 20.0 x 6.00

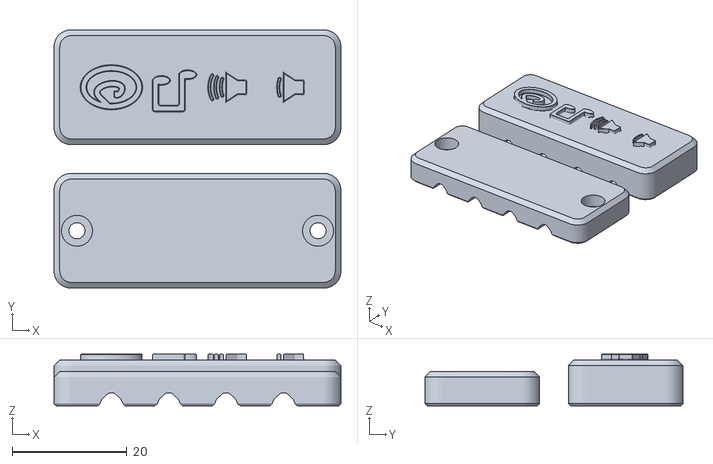
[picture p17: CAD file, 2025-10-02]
Toy_Instructions/Sound_Movement_Light/Dimple_Peek_a_Boo_Elephant_Bunny/3D_Printing_Files/Dimple_Peep_a_Book_Elephant_Bunny_Cable_Clamp.stl
50.0 x 45.0 x 9.00

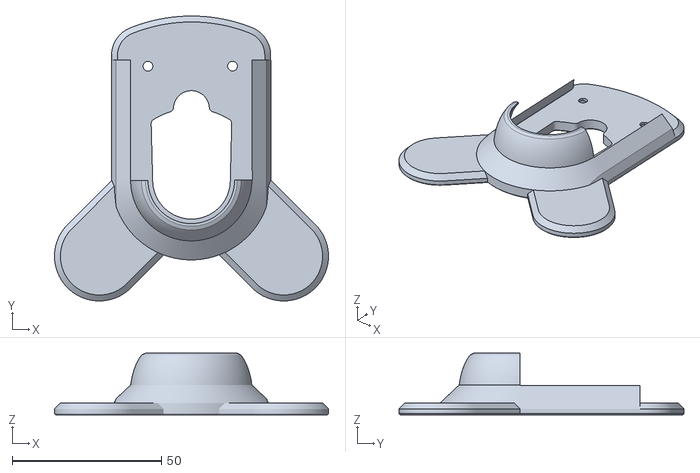
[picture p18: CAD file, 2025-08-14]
Toy_Instructions/Sound_Movement_Light/Kid_Connection_Spinning_Light_Wand/Battery_Interrupter_Maker_Guide/3D_Print_Files/LightWand_Base_v1.2.stl
91.8 x 95.4 x 20.6

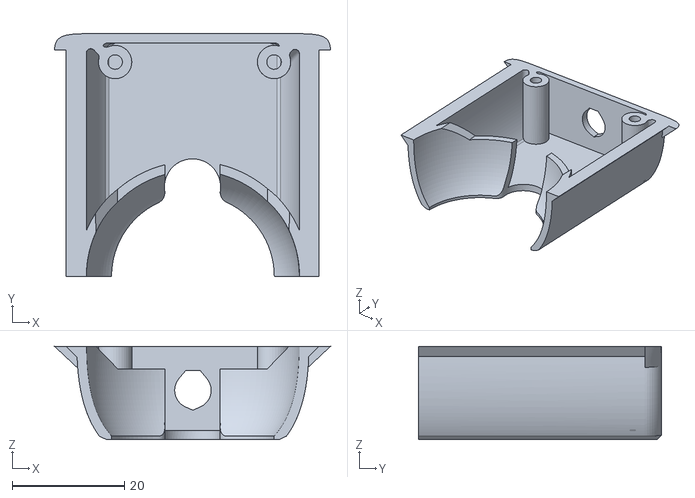
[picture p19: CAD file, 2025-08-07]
Toy_Instructions/Sound_Movement_Light/Kid_Connection_Spinning_Light_Wand/Mono_Jack_Maker_Guide/3D_Print_Files/V1.1/Jack_Cover.stl
49.2 x 43.3 x 16.6

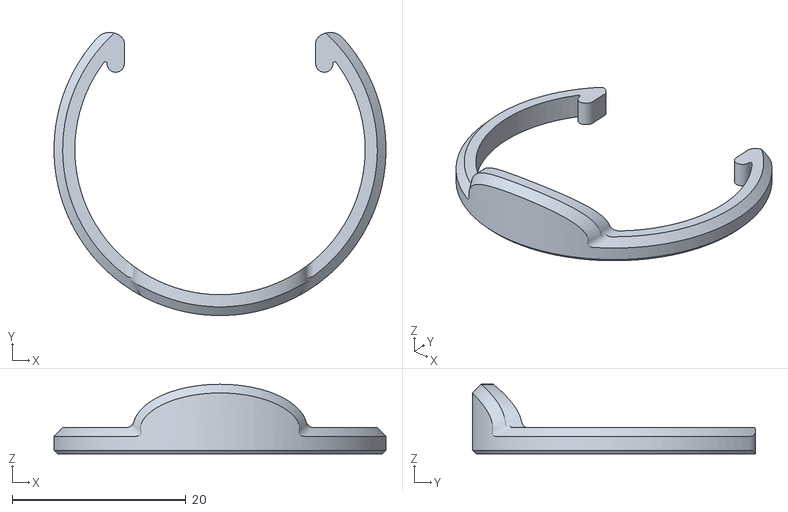
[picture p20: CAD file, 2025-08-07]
Toy_Instructions/Sound_Movement_Light/Toysery_Spinning_Light_Up_Wand/3D_Printing_Files/Light_Wand_Button_Clamp_for_Battery_Interruptor.stl
38.2 x 32.6 x 8.00

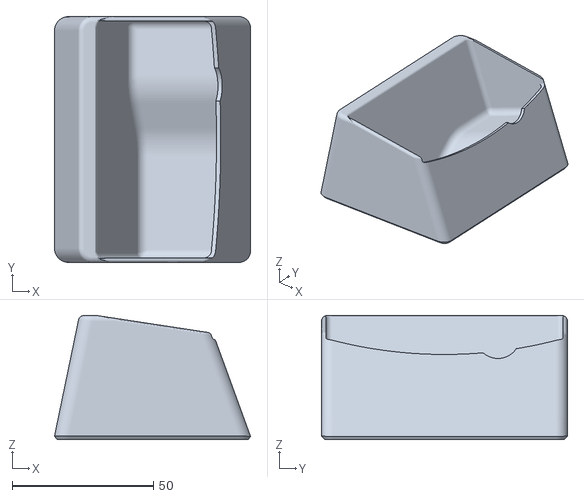
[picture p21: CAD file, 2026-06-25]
Toy_Instructions/Sound_Movement_Light/Weofferwhatyouwant_First_Guitar/3D_Print_Files/First_Guitar_toy_stand.stl
69.3 x 87.0 x 43.9

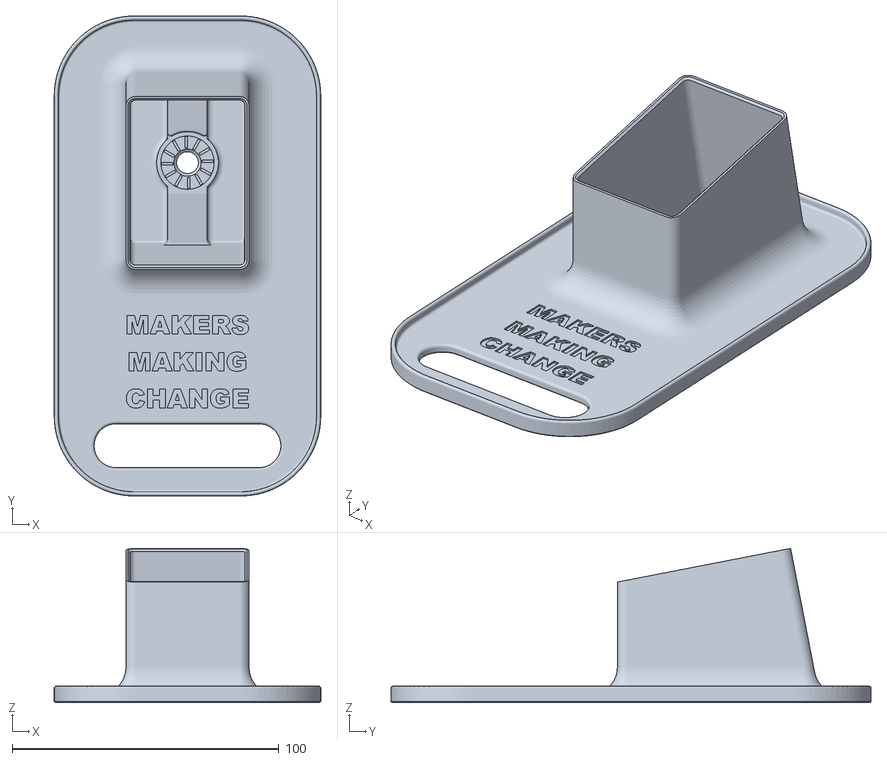
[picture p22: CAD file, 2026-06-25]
Toy_Instructions/Water_Nerf_Gun/Zuru_XShotMotorSoaker_Water_Gun/3D_Printing_Files/Water_Gun_Stand_ZURU_XSHOT_Motor_Soaker.stl
100.0 x 180.0 x 57.8

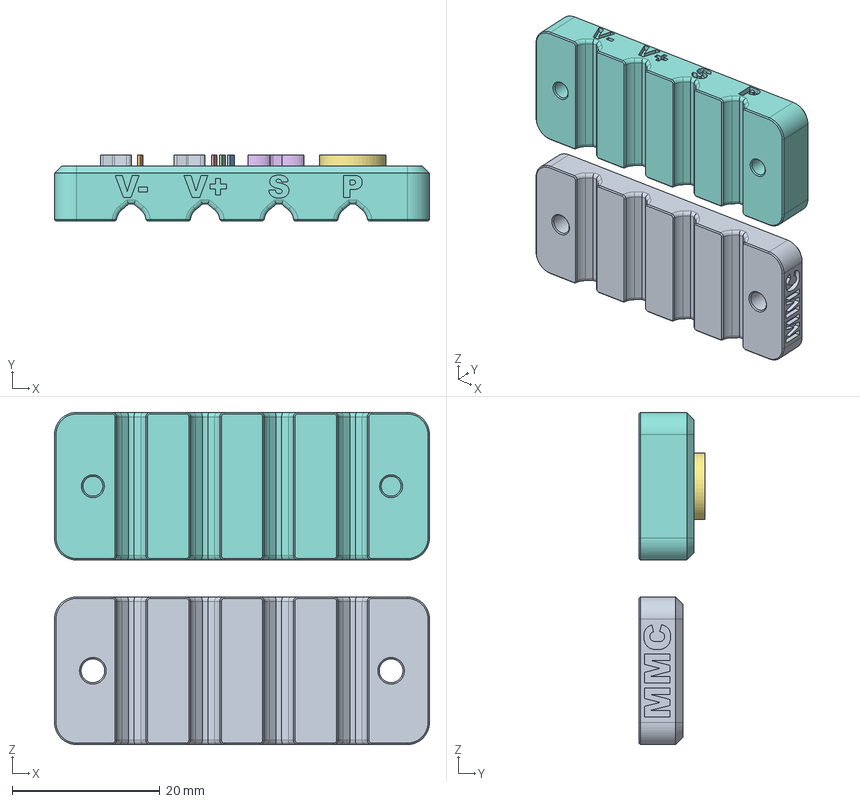
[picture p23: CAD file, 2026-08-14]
Resources/Cable_Clamp/Cable_Clamp_Dimple.step
50.8 x 9.00 x 45.0 mm
Volume_Down
Volume_Up
Song
Peek_A_Boo
Cable_Clamp_Bottom

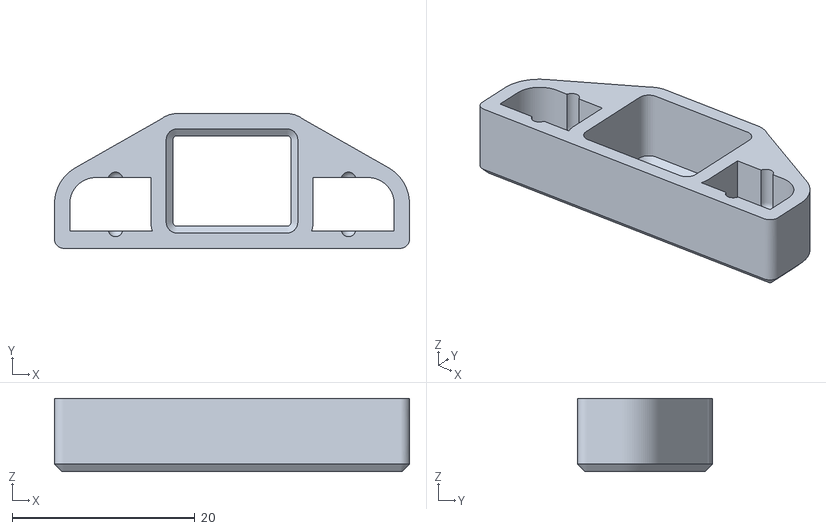
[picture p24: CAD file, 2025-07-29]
Toy_Instructions/Bubble/Playday_Light_Up_Bubble_Blaster/Battery_Interrupter_Maker_Guide/3D_Printing_Files/Cable_Tie_Holder_Front.stl
38.8 x 14.7 x 7.99

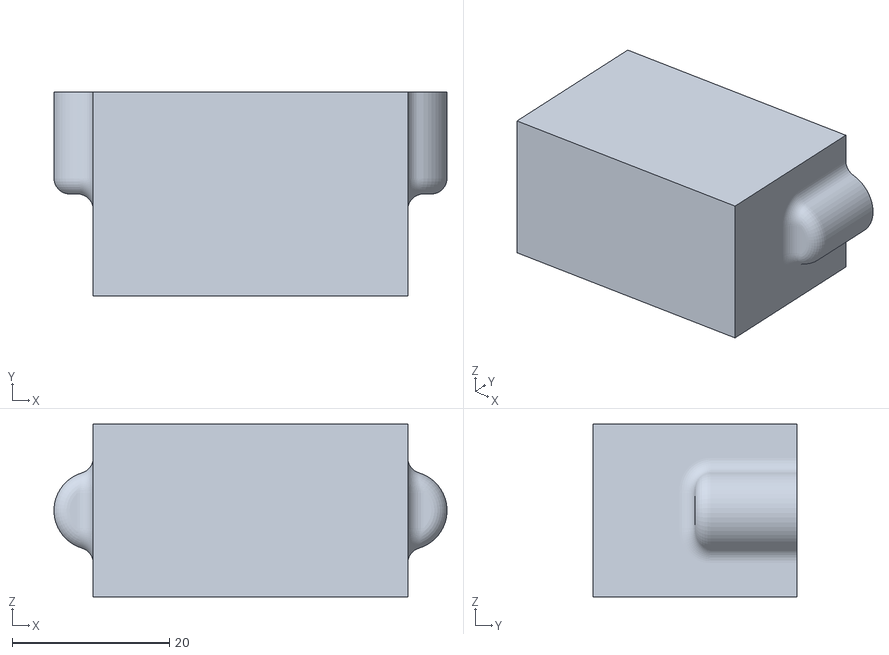
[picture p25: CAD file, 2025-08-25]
Toy_Instructions/RC/Estink_Rattle_Snake_Toy/3D_Printing_Files/monojackboxbase.stl
50.0 x 26.0 x 22.0

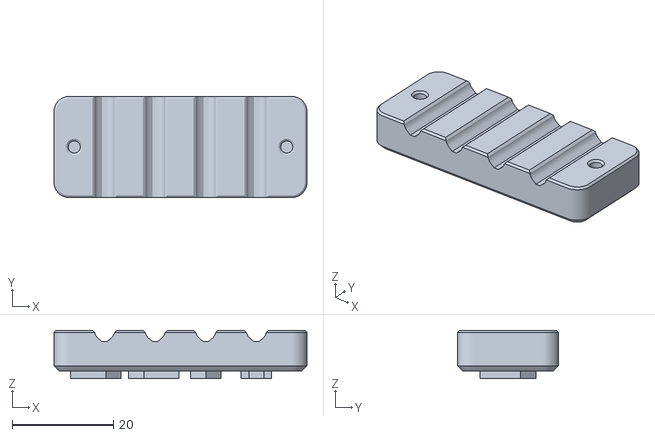
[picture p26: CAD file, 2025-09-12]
Toy_Instructions/RC/Monster_Jam_RC_Cars_Various/3D_Printing_Files/Cable_Clamp_Front.stl
50.0 x 20.0 x 9.50

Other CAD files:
Toy_Instructions/Sound_Movement_Light/Leapfrog_My_Pal_Scout_Violet/3D_Printing_Files/Cable-Clamp.stl
Toy_Instructions/Sound_Movement_Light/Kid_Connection_Spinning_Light_Wand/Battery_Interrupter_Maker_Guide/3D_Print_Files/LightWant_JackCover_v1.2.stl
Toy_Instructions/Sound_Movement_Light/Kid_Connection_Spinning_Light_Wand/Mono_Jack_Maker_Guide/3D_Print_Files/V1.1/Base.stl
Toy_Instructions/Sound_Movement_Light/Toysery_Spinning_Light_Up_Wand/3D_Printing_Files/Wand_Cover_v0.3.1.stl
Resources/Cable_Clamp/Cable_Clamp_Dimple.stl
Resources/Cable_Clamp/Cable_Clamp_FBLR.stl
Toy_Instructions/RC/Monster_Jam_RC_Cars_Various/CAD_Design_Files/Clamp v2 v11 v2.f3d
Toy_Instructions/Sound_Movement_Light/Kid_Connection_Spinning_Light_Wand/Mono_Jack_Maker_Guide/3D_Print_Files/V1.0/Base.stl
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

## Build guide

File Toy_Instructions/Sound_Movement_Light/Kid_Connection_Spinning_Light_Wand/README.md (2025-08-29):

# Spinning Light Wand Adaptation
The Spinning Light Wand Adaptation comprises instructions and files to adapt a commercially available Spinning Light Wand toy for use with an assistive switch. The toy is modified so that it has a 3.5 mm jack in place of the button. When a standard assistive switch with a 3.5 mm mono jack is attached and activated, the toy will activate. The toy is mounted into a 3D printed base that keeps the toy upright and houses the input jack. 

<p align="center">
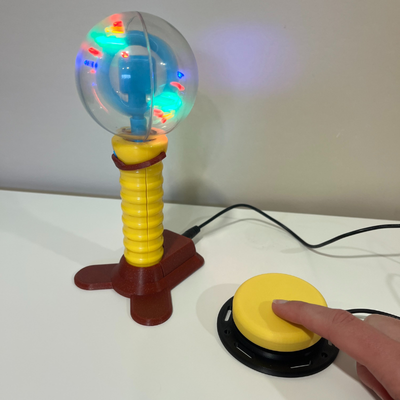
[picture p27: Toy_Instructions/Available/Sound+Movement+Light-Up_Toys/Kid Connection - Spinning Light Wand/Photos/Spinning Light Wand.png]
Picture of a switch adapted spinning light wand.
 
</p>

## More info at
- [Makers Making Change Project Page](https://makersmakingchange.com/project/spinning-light-wand-toy-adaptation/)

## Getting Started

### 1. Order the Off-The-Shelf Components

The [Bill of Materials]() lists all of the parts and components required to adapt the Spinning Light Wand. The toy is typically available at Walmart stores.

### 2. Print the 3D Printable components
Print the components. All of the files and individual print files can be in the [Build_Files](Build_Files) folder.

### 3. Assembly
Reference the [Assembly Guide v1.0](/Documentation/Spinning_Light_Wand_Assembly_Guide_V1.0.pdf) or [Assembly Guide v1.1](/Documentation/Spinning_Light_Wand_Assembly_Guide_V1.1.pdf) for the tools and steps required to build each portion.

## Files
### Documentation
| Document             | Version | Link |
|----------------------|---------|------|
| Design Rationale     | 1.1     | [Spinning_Light_WandDesign_Rationale]()     |
| Bill of Materials    | 1.1     | [Spinning_Light_Wand_Bill_of_Materials]()     |
| 3D Printing Guide    | 1.1     | [Spinning_Light_Wand_3D_Printing_Guide]()     |
| Assembly Guide       | 1.0     | [Spinning_Light_Wand_Assembly_Guide]()     |
| Assembly Guide       | 1.1     | [Spinning_Light_Wand_Assembly_Guide]()     |
| Maker Checklist      | 1.1     | [Spinning_Light_Wand_Maker_Checklist]()     |
| User Guide           | 1.0     | [Spinning_Light_Wand_User_Guide]()    |
| User Guide           | 1.1     | [Spinning_Light_Wand_User_Guide]()    |
| Changelog            | 1.1     | [Spinning_Light_Wand_Changelog]()     |

### Design Files
- [CAD Files](/Design_Files)

### Build Files
 - [3D Printing Files](/Build_Files)

## Attribution
This adaptation was designed by Mimi Xia of the [Makers Making Change Vancouver Chapter](https://vanhack.ca/wp/makers-making-change-vancouver-chapter/). 

3D Printed Wand Base v1.0 designed by Mimi Xia.

3D Printed Wand Base v1.1 designed by Jake McIvor – Makers Making Change.

Neil Squire / Makers Making Change assisted with the creation of the documentation.

## License
Everything needed or used to design, make, test, or prepare the Spinning Light Wand Adaptation is licensed under the CERN 2.0 Permissive license https://ohwr.org/project/cernohl/wikis/Documents/CERN-OHL-version-2 (CERN-OHL-P) .

Accompanying material such as instruction manuals, videos, and other copyrightable works that are useful but not necessary to design, make, test, or prepare the Spinning Light Wand Adaptation are published under a Creative Commons Attribution-NonCommercial-ShareAlike 4.0 license https://creativecommons.org/licenses/by-nc-sa/4.0/ (CC BY-NC-SA 4.0)

----

<!-- ABOUT MMC START -->
## About Makers Making Change
[Makers Making Change Logo](https://www.makersmakingchange.com/)

Makers Making Change is a program of [Neil Squire](https://www.neilsquire.ca/), a Canadian non-profit that uses technology, knowledge, and passion to empower people with disabilities.

Makers Making Change leverages the capacity of community based Makers, Disability Professionals and Volunteers to develop and deliver affordable Open Source Assistive Technologies.

 - Website: [www.MakersMakingChange.com](https://www.makersmakingchange.com/)
 - GitHub: [makersmakingchange](https://github.com/makersmakingchange)
 - Bluesky: [@makersmakingchange.bsky.social](https://bsky.app/profile/makersmakingchange.bsky.social)
 - Instagram: [@makersmakingchange](https://www.instagram.com/makersmakingchange)
 - Facebook: [makersmakechange](https://www.facebook.com/makersmakechange)
 - LinkedIn: [Neil Squire Society](https://www.linkedin.com/company/neil-squire-society/)
 - Thingiverse: [makersmakingchange](https://www.thingiverse.com/makersmakingchange/about)
 - Printables: [MakersMakingChange](https://www.printables.com/@MakersMakingChange)

### Contact Us
For technical questions, to get involved, or to share your experience we encourage you to [visit our website](https://www.makersmakingchange.com/) or [contact us](https://www.makersmakingchange.com/s/contact).
<!-- ABOUT MMC END -->

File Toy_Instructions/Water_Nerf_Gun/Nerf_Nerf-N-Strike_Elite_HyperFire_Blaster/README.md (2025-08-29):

# Switch Adapted Nerf N-Strike Hyperfire Blaster
The Switch Adapted Nerf Gun is designed to be a switch adapted toy for an older audience. The majority of switch adapted toys are designed for a younger audience, so this project aims to adapt a toy aimed at older children and make it switch accessible.



## More info at
- [Makers Making Change Project Page](https://www.makersmakingchange.com/product/switch-adapted-nerf-nstrike-hyperfire-blaster/01tJR000000694VYAQ)

## How to Obtain a Switch Adapted Nerf Gun
### 1. Do it Yourself (DIY) or Do it Together (DIT)

This is an open-source assistive technology, so anyone is free to build it. All of the files and instructions required to build the Switch Adapted Nerf Gun are contained within this repository. Refer to the Maker Checklist below.

### 2. Request a build of this device

If you would like to obtain a Switch Adapted Nerf Gun, you may submit a build request through the [MMC Library Page](https://www.makersmakingchange.com/request-a-device?id=01tJR000000694VYAQ). The requestor is responsible for the cost of materials and any shipping.

### 3. How to build this device for someone else

If you have the skills and equipment to build this device, and would like to donate your time to create the switch for someone who needs it, visit the [MMC Maker Wanted](https://makersmakingchange.com/maker-wanted/) section.

## Getting Started

### 1. Read the Makers Checklist

The Makers Checklist contains a list of tasks to complete to build the device.
[The Makers Checklist](/Documentation/Switch_Adapted_Nerf_Gun_Maker_Checklist_V1.0.pdf)

### 2. Order the Off-The-Shelf Components

The [Bill of Materials](/Documentation/Switch_Adapted_Nerf_Gun_BOM_V1.0.xlsx) lists all of the parts and components required to build the Switch Adapted Nerf Gun. The main gun component needs to be ordered online. The rest of the off-the-shelf components are also online or may be available in smaller quantities at your local hardware store or dollar store.

### 3. Print the 3D Printable components

All of the files and individual print files can be in the [/Build_Files/3D_Printing_Files](/Build_Files/3D_Printing_Files/) folder.

### 4. Assemble the Switch Adapted Nerf Gun

Reference the [Assembly Guide](/Documentation/Switch_Adapted_Nerf_Gun_Assembly_Guide_V1.0.pdf) for the tools and steps required to build each portion.

## Files
### Documentation
| Document             | Version | Link |
|----------------------|---------|------|
| Design Rationale     | 1.0     | [Switch_Adapted_Nerf_Gun_Design_Rationale](/Documentation/Switch_Adapted_Nerf_Gun_Design_Rationale_V1.0.pdf)     |
| Maker Checklist      | 1.0     | [Switch_Adapted_Nerf_Gun_Maker_Checklist](/Documentation/Switch_Adapted_Nerf_Gun_Maker_Checklist_V1.0.pdf)     |
| Bill of Materials    | 1.0     | [Switch_Adapted_Nerf_Gun_Bill_of_Materials](/Documentation/Switch_Adapted_Nerf_Gun_BOM_V1.0.xlsx)     |
| 3D Printing Guide    | 1.0     | [Switch_Adapted_Nerf_Gun_3D_Printing_Guide](/Documentation/Switch_Adapted_Nerf_Gun_3D_Printing_Guide_V1.0.pdf)     |
| Assembly Guide       | 1.0     | [Switch_Adapted_Nerf_Gun_Assembly_Guide](/Documentation/Switch_Adapted_Nerf_Gun_Assembly_Guide_V1.0.pdf)     |
| User Guide           | 1.0     | [Switch_Adapted_Nerf_Gun_User_Guide](/Documentation/Switch_Adapted_Nerf_Gun_User_Guide_V1.0.pdf)    |
| Changelog            | 1.0     | [Switch_Adapted_Nerf_Gun_Changelog](/Documentation/Switch_Adapted_Nerf_Gun_Changelog_V1.0.pdf)     |

### Design Files
[CAD Files](/Design_Files/CAD_Files)

### Build Files
 - [3D Printing Files](/Build_Files/3D_Printing_Files)

## Attribution
Designers:
 - Design by [Nicholas Stallings](https://www.youtube.com/watch?v=sFg3B8Z95hU)
 - Documentation by Neil Squire Society/Makers Making Change

## License
Everything needed or used to design, make, test, or prepare the Switch Adapted Nerf Gun is licensed under the [Attribution-NonCommercial-ShareAlike 4.0 ](https://creativecommons.org/licenses/by-nc-sa/4.0/).

Accompanying material such as instruction manuals, videos, and other copyrightable works that are useful but not necessary to design, make, test, or prepare the <Device-Name> are published under a Creative Commons Attribution-ShareAlike 4.0 license https://creativecommons.org/licenses/by-sa/4.0/ (CC BY-SA 4.0).

---
<!-- ABOUT MMC START -->
## About Makers Making Change
[Makers Making Change Logo](https://www.makersmakingchange.com/)

Makers Making Change is a program of [Neil Squire](https://www.neilsquire.ca/), a Canadian non-profit that uses technology, knowledge, and passion to empower people with disabilities.

Makers Making Change leverages the capacity of community based Makers, Disability Professionals and Volunteers to develop and deliver affordable Open Source Assistive Technologies.

 - Website: [www.MakersMakingChange.com](https://www.makersmakingchange.com/)
 - GitHub: [makersmakingchange](https://github.com/makersmakingchange)
 - Bluesky: [@makersmakingchange.bsky.social](https://bsky.app/profile/makersmakingchange.bsky.social)
 - Instagram: [@makersmakingchange](https://www.instagram.com/makersmakingchange)
 - Facebook: [makersmakechange](https://www.facebook.com/makersmakechange)
 - LinkedIn: [Neil Squire Society](https://www.linkedin.com/company/neil-squire-society/)
 - Thingiverse: [makersmakingchange](https://www.thingiverse.com/makersmakingchange/about)
 - Printables: [MakersMakingChange](https://www.printables.com/@MakersMakingChange)

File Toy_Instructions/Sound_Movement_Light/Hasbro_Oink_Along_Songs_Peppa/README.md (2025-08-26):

# Switch Adapted Hasbro Oink Along Songs Peppa Plush
The Switch Adapted Peppa Pig Toy is a switch adapted plush Peppa Pig toy that makes noises and sings songs when the switch is activated. 

<p align="center">
 Picture of a switch adapted plush Peppa Pig toy.
</p>

## More info at
- [Makers Making Change Project Page](https://makersmakingchange.com/project/switch-adapted-peppa-pig-toy/)

## How to Obtain a Switch Adapted Hasbro Oink Along Songs Peppa Plush
### 1. Do it Yourself (DIY) or Do it Together (DIT)

This is an open-source assistive technology, so anyone is free to build it. All of the files and instructions required to build the Switch Adapted Peppa Pig Toy are contained within this repository. Refer to the Maker Checklist below.

### 2. Request a build of this device

If you would like to obtain a Switch Adapted Peppa Pig Toy, you may submit a build request through the [MMC Library Page](https://www.makersmakingchange.com/product/switch-adapted-hasbro-oinkalong-songs-peppa-plush/01tJR000000694UYAQ). The requestor is responsible for the cost of materials and any shipping.

### 3. How to build this device for someone else

If you have the skills and equipment to build this device, and would like to donate your time to adapt a toy for someone who needs it, visit the [MMC Maker Wanted](https://makersmakingchange.com/maker-wanted/) section.

## Getting Started

### 1. Read the Makers Checklist

The Makers Checklist contains a list of tasks to complete to build the device.

### 2. Order the Off-The-Shelf Components

The [Bill of Materials](/Documentation/Peppa_Pig_BOM_v1.0.xlsx) lists all of the parts and components required to build the Switch Adapted Peppa Pig Toy. The main switch component needs to be ordered online. The rest of the off-the-shelf components are also online or may be available in smaller quantities at your local hardware store or dollar store.

### 3. Assemble the Switch Adapted Peppa Pig Toy

Reference the [Assembly Guide](/Documentation/Peppa_Pig_Assembly_Guide_v1.0.pdf) for the tools and steps required to build each portion.

## Files
### Documentation
| Document             | Version | Link |
|----------------------|---------|------|
| Design Rationale     | 1.0     | [Peppa Pig Design Rationale](https://github.com/makersmakingchange/Adapted-Toys/blob/bc86300f3b0eae2811bf68a4ef74ecb4e4579407/Toy_Instructions/Available_Toys/Sound%2BMovement%2BLight-Up_Toys/Hasbro%20-%20Oink-Along%20Songs%20Peppa%20Toy/Peppa_Pig_Design_Rationale_v1.0.pdf)     |
| Maker Checklist      | 1.0     | [Peppa_Pig_Maker_Checklist](/Peppa_Pig_Maker_Checklist_v1.0.pdf)     |
| Bill of Materials    | 1.0     | [Peppa_Pig_Bill_of_Materials](/Peppa_Pig_BOM_v1.0.xlsx)     |
| Assembly Guide       | 1.0     | [Peppa Pig Assembly Guide](https://github.com/makersmakingchange/Adapted-Toys/blob/9d625e8b73419c6701886cfb9ad90c898146936d/Toy_Instructions/Available_Toys/Sound%2BMovement%2BLight-Up_Toys/Hasbro%20-%20Oink-Along%20Songs%20Peppa%20Toy/Peppa_Pig_Assembly_Guide_v1.0.pdf)     |
| User Guide           | 1.0     | [Peppa_Pig_User_Guide](/Peppa_Pig_User_Guide_v1.0.pdf)    |
| Changelog            | 1.0     | [Peppa_Pig_Changelog](/Peppa_Pig_Changelog_v1.0.pdf)     |

## Attribution
Modification method and documentation created by Neil Squire / Makers Making Change.

## License
Everything needed or used to design, make, test, or prepare the Switch Adapted Peppa Pig Toy is licensed under the CERN 2.0 Permissive license <https://ohwr.org/cern_ohl_p_v2.txt> (CERN-OHL-P) . 

Accompanying material such as instruction manuals, videos, and other copyrightable works that are useful but not necessary to design, make, test, or prepare the Switch Adapted Peppa Pig Toy are published under a Creative Commons Attribution-ShareAlike 4.0 license https://creativecommons.org/licenses/by-sa/4.0/ (CC BY-SA 4.0).

---
<!-- ABOUT MMC START -->
## About Makers Making Change
[Makers Making Change Logo](https://www.makersmakingchange.com/)

Makers Making Change is a program of [Neil Squire](https://www.neilsquire.ca/), a Canadian non-profit that uses technology, knowledge, and passion to empower people with disabilities.

Makers Making Change leverages the capacity of community based Makers, Disability Professionals and Volunteers to develop and deliver affordable Open Source Assistive Technologies.

 - Website: [www.MakersMakingChange.com](https://www.makersmakingchange.com/)
 - GitHub: [makersmakingchange](https://github.com/makersmakingchange)
 - Bluesky: [@makersmakingchange.bsky.social](https://bsky.app/profile/makersmakingchange.bsky.social)
 - Instagram: [@makersmakingchange](https://www.instagram.com/makersmakingchange)
 - Facebook: [makersmakechange](https://www.facebook.com/makersmakechange)
 - LinkedIn: [Neil Squire Society](https://www.linkedin.com/company/neil-squire-society/)
 - Thingiverse: [makersmakingchange](https://www.thingiverse.com/makersmakingchange/about)
 - Printables: [MakersMakingChange](https://www.printables.com/@MakersMakingChange)

### Contact Us
For technical questions, to get involved, or to share your experience we encourage you to [visit our website](https://www.makersmakingchange.com/) or [contact us](https://www.makersmakingchange.com/s/contact).
<!-- ABOUT MMC END -->

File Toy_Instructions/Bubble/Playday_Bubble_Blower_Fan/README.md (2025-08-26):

# Switch Adapted Play Day Bubble Blower Fan
The Switch Adapted Bubble Blower Fan is a commercial toy modified for use with an assistive switch. The Switch Adapted Bubble Blower may be beneficial to someone who may have difficulty pressing the original small activation button due to its size, location, or required activation force.

Attach an assistive switch with a 3.5 mm plug to the 3.5 mm jack on the toy. When the assistive switch is activated, the toy will generate bubbles. 



<!-- ## How to Obtain a Switch Adapted Bubble Blower Fan -->
<!-- ### 1. Do it Yourself (DIY) or Do it Together (DIT) -->

<!-- This is an open-source assistive technology, so anyone is free to build it. All of the files and instructions required to build the Switch Adapted Bubble Blower Fan are contained within this repository. Refer to the Maker Checklist below. -->

<!-- ### 2. Request a build of this device -->

<!-- If you would like to obtain a Switch Adapted Bubble Blower Fan , you may submit a build request through the [MMC Library Page](https://makersmakingchange.com/project/switch-adapted-bubble-blower-fan/). The requestor is responsible for the cost of materials and any shipping. -->

<!-- ### 3. How to build this device for someone else -->

<!-- If you have the skills and equipment to build this device, and would like to donate your time to create the switch for someone who needs it, visit the [MMC Maker Wanted](https://makersmakingchange.com/maker-wanted/) section. -->

## Getting Started

### 1. Read the Makers Checklist

The Makers Checklist provides an outline of all the steps required to create the switch adapted toy.

### 2. Order the Off-The-Shelf Components

The [Bill of Materials](https://github.com/makersmakingchange/Adapted-Toys/blob/fbb5f4c7a2e73e375d4c18f5000931a1d9781dcc/Toy_Instructions/Unavailable_Toys/Bubble_Toys/Play%20Day%20-%20Bubble%20Blower%20Fan/BubbleBlowerFan_BOM_v1.0.csv) lists all of the parts and components required to build the device.

### 3. Assemble the Switch Adapted Bubble Blower Fan

Reference the [Assembly Guide](https://github.com/makersmakingchange/Adapted-Toys/blob/e83be27dd523403fe3f2d48fcf537f965dd8a77c/Toy_Instructions/Unavailable_Toys/Bubble_Toys/Play%20Day%20-%20Bubble%20Blower%20Fan/BubbleBlowerFan_Assembly_Guide_v1.0.pdf) for the tools and steps required.

## Files
### Documentation
| Document             | Version | Link |
|----------------------|---------|------|
| Design Rationale     | 1.0     | [BubbleBlowerFan_Design_Rationale](https://github.com/makersmakingchange/Adapted-Toys/blob/1931f9cb67a8b1fba6c0a3200f7994bdff5ee81f/Toy_Instructions/Unavailable/Bubble_Toys/Play%20Day%20-%20Bubble%20Blower%20Fan/BubbleBlowerFan_Design_Rationale_v1.0.pdf)     |
| Maker Checklist      | 1.0     | [BubbleBlowerFan_Maker_Checklist](https://github.com/makersmakingchange/Adapted-Toys/blob/e41b5d5adbd15e9c846961d4d69dca1c1ec11b31/Toy_Instructions/Unavailable/Bubble_Toys/Play%20Day%20-%20Bubble%20Blower%20Fan/BubbleBlowerFan_Maker_Checklist_v1.0.pdf)     |
| Bill of Materials    | 1.0     | [BubbleBlowerFan_Bill_of_Materials](https://github.com/makersmakingchange/Adapted-Toys/blob/c3f81d556f39a5e2b94ecce2078a7b4216b3b0ac/Toy_Instructions/Unavailable/Bubble_Toys/Play%20Day%20-%20Bubble%20Blower%20Fan/BubbleBlowerFan_BOM_v1.0.csv)     |
| Assembly Guide       | 1.0     | [BubbleBlowerFan_Assembly_Guide](https://github.com/makersmakingchange/Adapted-Toys/blob/aa8dd7aac22343b3fd63df6ecd96fcd0daa42358/Toy_Instructions/Unavailable/Bubble_Toys/Play%20Day%20-%20Bubble%20Blower%20Fan/BubbleBlowerFan_Assembly_Guide_v1.0.pdf)     |
| User Guide           | 1.0     | [BubbleBlowerFan_User_Guide](https://github.com/makersmakingchange/Adapted-Toys/blob/4398fb44fc0f6c25e6e5d1e37ff028c973f4460d/Toy_Instructions/Unavailable/Bubble_Toys/Play%20Day%20-%20Bubble%20Blower%20Fan/BubbleBlowerFan_User_Guide_v1.0.pdf)    |
| Changelog            | 1.0     | [BubbleBlowerFan_Changelog](https://github.com/makersmakingchange/Adapted-Toys/blob/633b80fddd402c26effb28d6d75b34634b14aeb9/Toy_Instructions/Unavailable/Bubble_Toys/Play%20Day%20-%20Bubble%20Blower%20Fan/BubbleBlowerFan_Changelog_v1.0.pdf)    |

## Attribution
Modification method and documentation created by Neil Squire / Makers Making Change.

## License
Everything needed or used to design, make, test, or prepare the Switch Adapted Bubble Blower Fan is licensed under the CERN 2.0 Permissive license <https://ohwr.org/cern_ohl_p_v2.txt> (CERN-OHL-P) . 

Accompanying material such as instruction manuals, videos, and other copyrightable works that are useful but not necessary to design, make, test, or prepare the Switch Adapted Bubble Blower Fan are published under a Creative Commons Attribution-ShareAlike 4.0 license https://creativecommons.org/licenses/by-sa/4.0/ (CC BY-SA 4.0).

<!-- ABOUT MMC START -->
## About Makers Making Change
[Makers Making Change Logo](https://www.makersmakingchange.com/)

Makers Making Change is a program of [Neil Squire](https://www.neilsquire.ca/), a Canadian non-profit that uses technology, knowledge, and passion to empower people with disabilities.

Makers Making Change leverages the capacity of community based Makers, Disability Professionals and Volunteers to develop and deliver affordable Open Source Assistive Technologies.

 - Website: [www.MakersMakingChange.com](https://www.makersmakingchange.com/)
 - GitHub: [makersmakingchange](https://github.com/makersmakingchange)
 - Bluesky: [@makersmakingchange.bsky.social](https://bsky.app/profile/makersmakingchange.bsky.social)
 - Instagram: [@makersmakingchange](https://www.instagram.com/makersmakingchange)
 - Facebook: [makersmakechange](https://www.facebook.com/makersmakechange)
 - LinkedIn: [Neil Squire Society](https://www.linkedin.com/company/neil-squire-society/)
 - Thingiverse: [makersmakingchange](https://www.thingiverse.com/makersmakingchange/about)
 - Printables: [MakersMakingChange](https://www.printables.com/@MakersMakingChange)

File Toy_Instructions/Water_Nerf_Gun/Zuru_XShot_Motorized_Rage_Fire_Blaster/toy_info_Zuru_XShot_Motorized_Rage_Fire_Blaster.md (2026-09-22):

---
# Fill in the value after each colon, on the SAME line as the field -
# don't press Enter partway through a value. Leave a field completely
# blank (nothing after the colon) if you don't have that info yet.
last_updated:               # yyyy-mm-dd - date this file was last updated
toy_features:                # keep only the relevant lines below, delete the rest
  - Movement
  - Blaster
activation_type:            # keep only the relevant lines below, delete the rest
  - Press and Hold
requires_3d_printing: No    # Yes or No
adaptation_method:          # keep only the relevant lines below, delete the rest
  - Mono Jack + Wire
number_of_switches:         # keep only the relevant lines below, delete the rest
  - 2
hfth_collection_year: 2026      # e.g. 2026 - leave blank if never part of a HFTH collection
available_to_purchase: Yes  # Yes or No - is the toy still available to purchase?
toy_purchase_link: https://www.walmart.ca/en/ip/XSHOT-Insanity-Motorized-Rage-Fire-72-Darts-by-ZURU/6000207153516         # adds a "Where to Buy This Toy" button if filled in
toy_purchase_link_alt: https://www.canadiantire.ca/en/pdp/x-shot-insanity-s1-motorised-rage-fire-dart-blaster-ages-8-1500754p.html     # adds a 2nd purchase button if there's another link
general_notes: Difficult adaptation, a lot of screws and a lot of moving parts              # any general notes, e.g. "Uses lots of screws."
device_uid:                  # internal MMC use only - never shown on the site
name:                        # only fill in to OVERRIDE the auto name - else leave blank
category:                    # only fill in to OVERRIDE the auto category - else leave blank
link:                        # only fill in to OVERRIDE the auto GitHub link - else leave blank
battery_type:
battery_required:
battery_included:            # number of batteries included
contributers: Josie Versloot - Makers Making Change               # names of contributers to the instructions / this design
---

Every child deserves to play. But for many kids with disabilities, toys can be hard to use independently, and commercially adapted versions can run upwards of $300. However, with a little bit of tinkering, we can switch-adapt toys and make them accessible for a fraction of the cost.

Annually, from September to December Makers Making Change hosts the [Hacking for the Holidays](https://www.makersmakingchange.com/hacking-for-the-holidays) campaign, where we engage volunteers — students, corporate partners, and other community members — in many build events across Canada to help us adapt and donate thousands of toys and switches to families and clinicians all over Canada.

Please note the information on this page is only accurate to when it was last updated.

If you are looking for more information on where to purchase the materials to adapt a toy, please visit the [Common Component and Tool page](https://makersmakingchange.github.io/Switch_Adapted_Toys/toy-components-and-tools/) on this resource.

<!--
  Everything above this line (outside the --- --- block at the top) is
  just for humans reading this file - it isn't read by the site build.
  This same text already shows automatically on every toy's page, so you
  don't need to copy/edit it per toy; it's here for context only.

  ONE IMPORTANT RULE for the fields inside the --- --- block above:
  keep every value on the SAME line as its field name. If a value
  wraps onto a second line by accident (e.g. a long name spilling onto
  a new line without quotes), that whole wrapped block gets silently
  read as one long piece of text - which can also swallow the field(s)
  that come right after it. If you ever need to double check a field
  looks right, open this file on GitHub and confirm nothing after a
  colon spills onto its own new line unless it's a "- " list item.
-->

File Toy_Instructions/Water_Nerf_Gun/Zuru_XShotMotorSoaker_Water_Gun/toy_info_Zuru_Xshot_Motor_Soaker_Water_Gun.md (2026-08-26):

---
# Fill in the value after each colon, on the SAME line as the field -
# don't press Enter partway through a value. Leave a field completely
# blank (nothing after the colon) if you don't have that info yet.
last_updated: 2026-08-26               # yyyy-mm-dd - date this file was last updated
toy_features:                # keep only the relevant lines below, delete the rest
  - Water
activation_type:            # keep only the relevant lines below, delete the rest
  - Press and Hold
requires_3d_printing: Yes    # Yes or No
adaptation_method:          # keep only the relevant lines below, delete the rest
  - Mono Jack + Wire
number_of_switches:         # keep only the relevant lines below, delete the rest
  - 1
hfth_collection_year: 2026       # e.g. 2026 - leave blank if never part of a HFTH collection
available_to_purchase: Yes  # Yes or No - is the toy still available to purchase?
toy_purchase_link: https://www.amazon.ca/XSHOT-Water-Turbo-Stream-Soaker/dp/B0FJJ33G75/ref=sr_1_6          # adds a "Where to Buy This Toy" button if filled in
toy_purchase_link_alt: https://www.walmart.ca/en/ip/XSHOT-Water-Turbo-Stream-Motor-Soaker-23ft-Range-Motorized-Outdoor-Water-Blaster-by-ZURU-for-Kids-Teens-Adults-Ages-8/64XPWS1I66TI      # adds a 2nd purchase button if there's another link
general_notes: Moderate- lots of screws               # any general notes, e.g. "Uses lots of screws."
device_uid:                  # internal MMC use only - never shown on the site
name:                        # only fill in to OVERRIDE the auto name - else leave blank
category:                    # only fill in to OVERRIDE the auto category - else leave blank
link:                        # only fill in to OVERRIDE the auto GitHub link - else leave blank
battery_type: AA
battery_required: 4
battery_included:
---

Every child deserves to play. But for many kids with disabilities, toys can be hard to use independently, and commercially adapted versions can run upwards of $300. However, with a little bit of tinkering, we can switch-adapt toys and make them accessible for a fraction of the cost.

Annually, from September to December Makers Making Change hosts the [Hacking for the Holidays](https://www.makersmakingchange.com/hacking-for-the-holidays) campaign, where we engage volunteers — students, corporate partners, and other community members — in many build events across Canada to help us adapt and donate thousands of toys and switches to families and clinicians all over Canada.

Please note the information on this page is only accurate to when it was last updated.

If you are looking for more information on where to purchase the materials to adapt a toy, please visit the [Common Component and Tool page](https://makersmakingchange.github.io/Switch_Adapted_Toys/toy-components-and-tools/) on this resource.

<!--
  Everything above this line (outside the --- --- block at the top) is
  just for humans reading this file - it isn't read by the site build.
  This same text already shows automatically on every toy's page, so you
  don't need to copy/edit it per toy; it's here for context only.

  ONE IMPORTANT RULE for the fields inside the --- --- block above:
  keep every value on the SAME line as its field name. If a value
  wraps onto a second line by accident (e.g. a long name spilling onto
  a new line without quotes), that whole wrapped block gets silently
  read as one long piece of text - which can also swallow the field(s)
  that come right after it. If you ever need to double check a field
  looks right, open this file on GitHub and confirm nothing after a
  colon spills onto its own new line unless it's a "- " list item.
-->

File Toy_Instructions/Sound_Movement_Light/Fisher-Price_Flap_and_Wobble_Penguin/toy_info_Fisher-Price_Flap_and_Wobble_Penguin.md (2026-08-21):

---
# Fill in the value after each colon, on the SAME line as the field -
# don't press Enter partway through a value. Leave a field completely
# blank (nothing after the colon) if you don't have that info yet.
last_updated: 2026-08-21               # yyyy-mm-dd - date this file was last updated
toy_features:                # keep only the relevant lines below, delete the rest
  - Movement
  - Sound
activation_type:            # keep only the relevant lines below, delete the rest
  - Single Press
requires_3d_printing: No    # Yes or No
adaptation_method:          # keep only the relevant lines below, delete the rest
  - Mono Cable
number_of_switches:         # keep only the relevant lines below, delete the rest
  - 1
hfth_collection_year: 2026       # e.g. 2026 - leave blank if never part of a HFTH collection
available_to_purchase: Yes  # Yes or No - is the toy still available to purchase?
toy_purchase_link: https://a.co/d/2Y4kcvO          # adds a "Where to Buy This Toy" button if filled in
toy_purchase_link_alt:      # adds a 2nd purchase button if there's another link
general_notes: Soldering on PCB               # any general notes, e.g. "Uses lots of screws."
device_uid:                  # internal MMC use only - never shown on the site
name:                        # only fill in to OVERRIDE the auto name - else leave blank
category:                    # only fill in to OVERRIDE the auto category - else leave blank
link:                        # only fill in to OVERRIDE the auto GitHub link - else leave blank
battery_type: AA
battery_required: 4
battery_included:
---

Every child deserves to play. But for many kids with disabilities, toys can be hard to use independently, and commercially adapted versions can run upwards of $300. However, with a little bit of tinkering, we can switch-adapt toys and make them accessible for a fraction of the cost.

Annually, from September to December Makers Making Change hosts the [Hacking for the Holidays](https://www.makersmakingchange.com/hacking-for-the-holidays) campaign, where we engage volunteers — students, corporate partners, and other community members — in many build events across Canada to help us adapt and donate thousands of toys and switches to families and clinicians all over Canada.

Please note the information on this page is only accurate to when it was last updated.

If you are looking for more information on where to purchase the materials to adapt a toy, please visit the [Common Component and Tool page](https://makersmakingchange.github.io/Switch_Adapted_Toys/toy-components-and-tools/) on this resource.

<!--
  Everything above this line (outside the --- --- block at the top) is
  just for humans reading this file - it isn't read by the site build.
  This same text already shows automatically on every toy's page, so you
  don't need to copy/edit it per toy; it's here for context only.

  ONE IMPORTANT RULE for the fields inside the --- --- block above:
  keep every value on the SAME line as its field name. If a value
  wraps onto a second line by accident (e.g. a long name spilling onto
  a new line without quotes), that whole wrapped block gets silently
  read as one long piece of text - which can also swallow the field(s)
  that come right after it. If you ever need to double check a field
  looks right, open this file on GitHub and confirm nothing after a
  colon spills onto its own new line unless it's a "- " list item.
-->

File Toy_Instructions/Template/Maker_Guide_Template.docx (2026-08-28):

# Completion Checklist (DELETE BEFORE POSTING)

- Download a copy of this template
  - Rename it Manufactuer_Name_Toy_Name_Maker_Guide
- Decide how the toy will be adapted
  - Choose from mono jack, mono cable and battery interrupter methods
  - Delete the highlighted headers, other two sets of instructions and Table of Contents
- Update <MONTH> and <YEAR> in header
- Update V<X.Y.Z> in header
- Update <TOY NAME> in header
- Update <YEAR> in footer
- Update <Author> in footer
- Update Required Components table
  - Add a photo of the toy from the manufacturer’s website
  - Add or remove component images as necessary
  - Add the toy’s manufacturer name and name to the BOM
  - Adjust the number of batteries in the BOM and image
- Add tools to Tool List
  - Specify screwdriver type
- Add Required PPE
- Complete Assembly Instructions
  - Edit and add steps as necessary
  - Add text to the left and images to the right
  - Add colored circles to the images to highlight what you’re referring to
- Delete Completion Checklist
- Before putting the toy back in the packaging
  - Take an image of the adapted toy with an assistive switch
  - This image will be used for the website

Download the template

File > Download > Word (.docx)

# Mono Jack Instructions

# Required Components

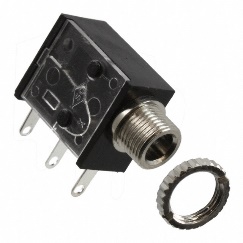
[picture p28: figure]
A rectangular mono jack with a silver ring.

1. <Toy Image> | | BOM 1. <Brand Name - Toy Name> (Store) 2. 3.5 mm Mono Jack and Ring 3. 22 AWG Wire 4. Electrical Tape 5. # and type of Batteries (please also adjust # of batteries in the photo) Refer to the Tool and Component List (https://www.makersmakingchange.com/toy-adapting-components-and-tools) for purchasing details.

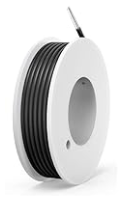
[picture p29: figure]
A roll of AWG wire
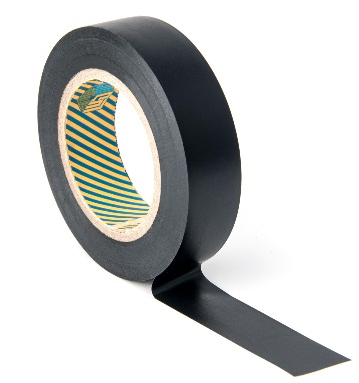
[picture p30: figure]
A roll of black electrical tape.

# Required Tools

- Small Phillips Screwdriver 3mm Diameter
- Ruler
- Wire strippers
- Soldering iron and solder
- Drill and 1/4” drill bit

# Required Personal Protective Equipment (PPE)

- Safety glasses

# Assembly Instructions

1. Carefully remove the toy from its packaging without damaging it (we will be repackaging the toy after adapting). Locate and remove the screws along the body of the toy. *Note: keep screws, and keep track of where they came from if there are multiple different sized screws | [Image]
2. Carefully separate the two halves of the toy. | [Image]

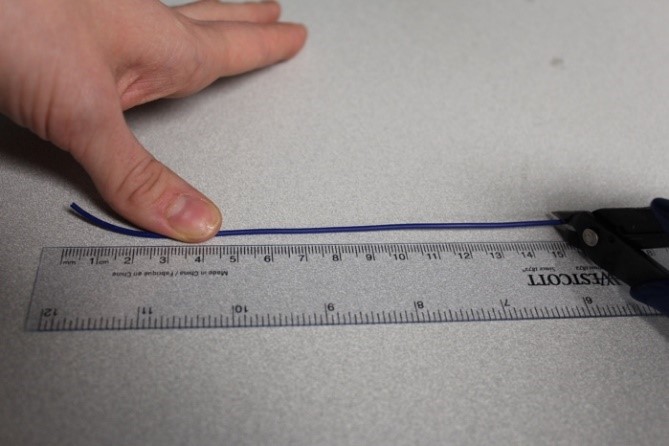
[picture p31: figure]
A person using a ruler to measure the length of a wire

3. Cut 2 pieces of wire, each X cm long.

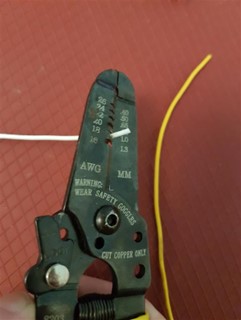
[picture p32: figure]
A wire stripper removing the insulation from a wire.

4. Use wire strippers to strip approximately 0.5 cm off each end of the wires

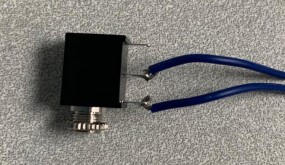
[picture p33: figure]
A rectangular mono cable with two wires soldering onto the front two tabs

5. Solder the two wires onto the front two tabs of the mono jack.

SELECT WHICH WAY THE TOY WILL BE ADAPTED AND DELETE THE OTHER SET

FOR TOYS ADAPTED IN PARALLEL

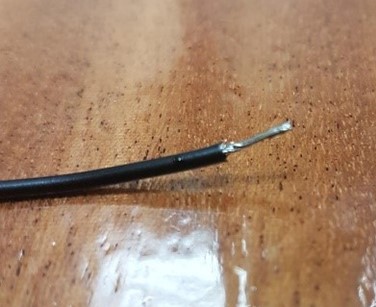
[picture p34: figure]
Solder melted onto the end of an exposed wire.

6. Tin the other ends of the wires by adding a small amount of solder to each wire.
7. Solder the new wires in parallel with the existing wires connected to the switch. Do this by carefully soldering the new wires on top of the existing wires, being careful not to break the original connection. | [Image]

8. It is now time to test the toy. Insert batteries into the battery compartment and an assistive switch into the mono jack. Test to make sure that the toy can be controlled using the original switch and the assistive switch.

Notes:

- If the toy does not turn on, please check the soldered connections.

[Select one statement]

For Continuous Toys (singing for example)]:

- If the toy continuously repeats the song when the switch is released, the connection is shorted. Check for areas of touching solder and separate using a soldering iron.

For Press Activation Toys (release and stop)

- If the toy does not turn off when the switch is released, the connection is shorted. Check for areas of touching solder and separate using a soldering iron.

[Image]

FOR TOYS ADAPTED IN SERIES
9. Locate a wire that connects from the battery compartment to the switch. Use the soldering iron to heat up the original solder and release the wire from the board. | [Image]
10. Solder the end of the released wire to one end of the wire connected to the mono jack. | [Image]
11. Wrap the exposed joint in electrical tape to ensure they stay connected. | [Image]
12. Solder the end of the other wire connected to the mono jack to the board where the wire was removed. | [Image]

13. It is now time to test the toy. Insert batteries into the battery compartment and an assistive switch into the mono jack. The toy will activate when the assistive switch is pressed.

Notes:

- If the toy does not turn on, please check the soldered connections.

[Select one statement]

For Continuous Toys (singing for example)]:

- If the toy continuously repeats the song when the switch is released, the connection is shorted. Check for areas of touching solder and separate using a soldering iron.

For Press Activation Toys (release and stop)

- If the toy does not turn off when the switch is released, the connection is shorted. Check for areas of touching solder and separate using a soldering iron.

[Image]

CONTINUE WITH THESE INSTRUCTIONS
14. Using a ¼” drill bit, drill a hole into the position shown on the right. Remove any loose plastic. | [Image]
15. Remove the retaining ring from the mono jack and push the mono jack through the hole from the inside. Reinstall the retaining ring on the outside of the toy and tighten to secure. | [Image]
16. Reassemble the toy using the screws set aside earlier. | [Image]
17. Test the toy again. If it is still working properly, repackage the toy and the adapted toy is complete! | [Image]

# Mono Cable Instructions

# Required Components

1. <Toy Image> | 2. | BOM 1. <Brand Name - Toy Name> 2. 3.5 mm Female Mono Cable 3. Cable Tie 4. # and type of Batteries (please also adjust # of batteries in the photo) Refer to the Tool and Component List (https://www.makersmakingchange.com/toy-adapting-components-and-tools) for purchasing details.

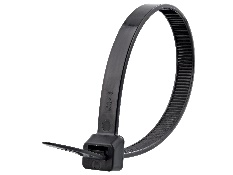
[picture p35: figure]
A cable tie.

# Required Tools

- Screwdriver (Please specify screwdriver type)
- Wire strippers
- Soldering iron and solder
- Drill and 1/8” drill bit
- Slip joint pliers
- Flush cutters

# Required Personal Protective Equipment (PPE)

- Safety glasses

# Assembly Instructions

1. Carefully remove the toy from its packaging without damaging it (we will be repackaging the toy after adapting). Locate and remove the screws along the body of the toy. *Note: keep screws, and keep track of where they came from if there are multiple different sized screws | [Image]
2. Carefully separate the two halves of the toy. | [Image]

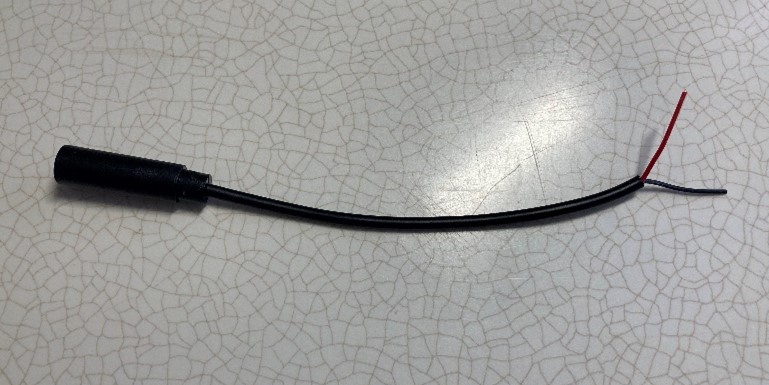
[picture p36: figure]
A mono cable with the two inner wires showing at the end

3. Use wire strippers to strip approximately 2 cm off the outer wire casing, revealing two internal wires.

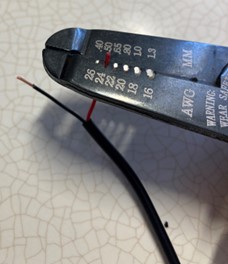
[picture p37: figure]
Wire strippers removing the insultation from a wire.

4. If there are 2 internal wires, strip approximately 0.5 cm off each wire.

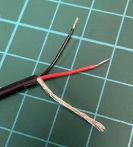
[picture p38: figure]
A cable that has three inner wires, red, black and exposed.
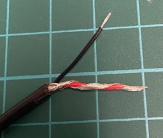
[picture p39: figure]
Exposed wire wrapped about the red wire

5. If there are three internal wires (red, black, and exposed), strip off 0.5 cm of the red insulation and twist the red wire and exposed wire together. Strip 0.5 cm from the black wire.
6. Melt a small amount of solder over the exposed ends of the wire.
7. Using a 1/8” drill bit, drill a hole into the position shown on the right. Remove any loose plastic and insert the mono cable through the hole. | [Image]
8. Attach the mono cable to the toy. | [Image]

9. It is now time to test the toy. Insert batteries into the battery compartment and an assistive switch into the mono jack. The toy will activate when the assistive switch is pressed.

Notes:

- If the toy does not turn on, please check the soldered connections.

[Select one statement]

For Continuous Toys (singing for example)]:

- If the toy continuously repeats the song when the switch is released, the connection is shorted. Check for areas of touching solder and separate using a soldering iron.

For Press Activation Toys (release and stop)

- If the toy does not turn off when the switch is released, the connection is shorted. Check for areas of touching solder and separate using a soldering iron.

[Image]
10. Attach a cable tie to the cable on the inside of the case as close as possible to where it enters. Tighten the cable tie as much as you can and snip the excess zip tie using the flush cutters. The cable tie will serve as strain relief, so the soldered connections do not get pulled and break.
11. Reassemble the toy using the screws set aside earlier. | [Image]
12. Test the toy again. If it is still working properly, repackage the toy and the adapted toy is complete! | [Image]

# Battery Interrupter Template

# Required Components

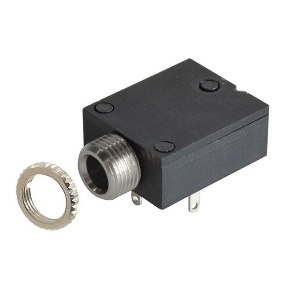
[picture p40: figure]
A flat rectangular mono jack with a silver ring.

1. <Toy Image> | | BOM 1. <Brand Name - Toy Name> 2. 3.5 mm Square Mono Jack and Ring 3. MMC Flex PCB 4. # and type of Batteries (please also adjust # of batteries in the photo) Refer to the Tool and Component List (https://www.makersmakingchange.com/toy-adapting-components-and-tools) for purchasing details.

# Required Tools

- Screwdriver (Please specify screwdriver type)
- Soldering iron and solder
- Scissors

# Required Personal Protective Equipment (PPE)

- Safety glasses

# Assembly Instructions

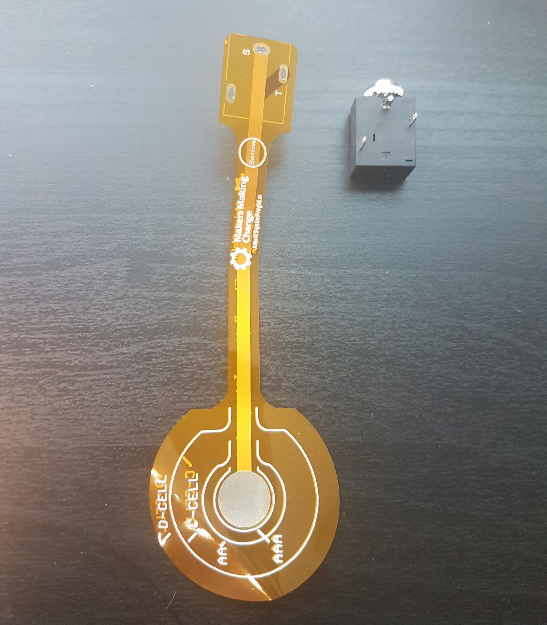
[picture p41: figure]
A flex printed circuit board and a flat rectangular mono jack.

1. Locate your battery interrupter PCB and mono jack. The prongs from the mono jack match up with the holes in the PCB. Lay the battery interrupter on top of the mono jack, with the metal prongs sticking through the holes.

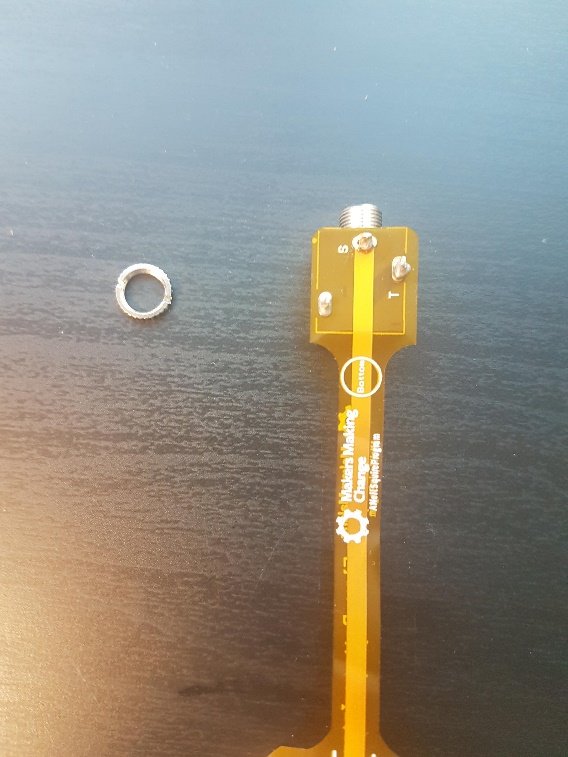
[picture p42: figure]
Printed circuit board placed over a flat rectangular mono jack and soldered in three places.

2. At the base, add solder to the metal prongs so the PCB and mono jack are connected. Make sure the PCB is as flat against the mono jack as possible. The metal ring that is around the input of the mono jack can be removed and set aside.

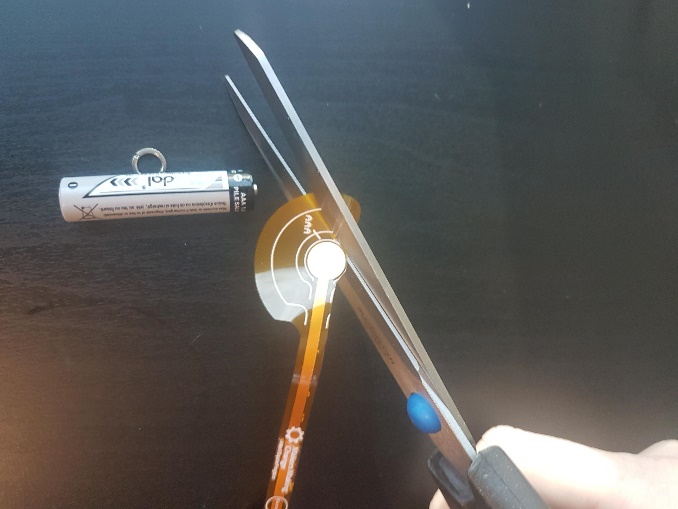
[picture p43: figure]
A pair of scissors cutting the printed circuit board.

3. Check what size the batteries are of the toy you wish to use the interrupter with. This toy uses AAA batteries. There are circles on the orange PCB indicating the battery size. Locate the circle labeled AAA and cut the PCB to that size.
4. Unscrew the battery cover from the toy. Match the circle that you just cut with the positive end of one of the batteries. Hold in place and replace the battery cover. Tighten the battery cover tightly to make sure the interrupter is pushed up against the battery. *Note: When it is secure enough, the toy will not turn on with the original button. | [Image for step 4]
5. The toy can now be paired with an assistive switch. When the switch is plugged in and activated, the toy should turn on. Repackage the toy and the adapted toy is complete! *Note: If the toy does not work, make sure the original button is on, and check the position of the interrupter. | [Image of the completed toy]

© <YEAR> by <AUTHOR> OR <Neil Squire>. This work is licensed under the CC BY SA 4.0 License: http://creativecommons.org/licenses/by-sa/4.0 Files available at https://github.com/makersmakingchange/Switch_Adapted_Toys Page 1 of 1

V<X.Y.Z> | <MONTH> <YEAR> Switch Adapted <TOY NAME> MAKER GUIDE

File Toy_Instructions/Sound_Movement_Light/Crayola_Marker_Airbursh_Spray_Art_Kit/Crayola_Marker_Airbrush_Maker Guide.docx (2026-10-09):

# Required Components

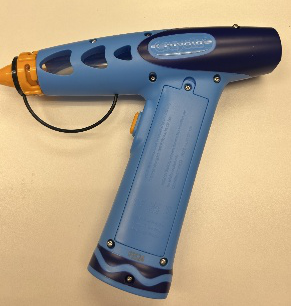
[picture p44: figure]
A rectangular mono jack with a silver ring.

| | BOM 1. Crayola Marker Airbrush Spray Art Kit (Amazon (https://www.amazon.ca/Crayola-45205-Marker-Airbrush/dp/B0F6T2XWJL/ref=asc_df_B0F6T2XWJL), Walmart (https://www.walmart.ca/en/ip/Crayola-Marker-Airbrush-Art-Kit/1HPWVN49J48X)) 2. 3.5 mm Mono Jack and Ring 3. 22 AWG Wire 4. 4 AA Batteries Refer to the Tool and Component List (https://www.makersmakingchange.com/toy-adapting-components-and-tools) for purchasing details.

A roll of AWG wire

# Required Tools

- Triangle Screwdriver
- Small Phillips Screwdriver 3mm Diameter
- Ruler
- Wire strippers
- Soldering iron and solder
- Drill and 1/4” drill bit

# Required Personal Protective Equipment (PPE)

- Safety glasses

# Assembly Instructions

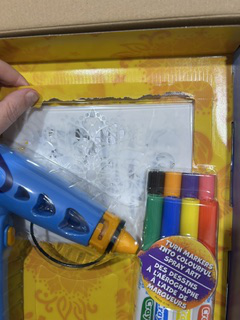
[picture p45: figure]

1. Carefully remove the toy from its packaging without damaging it (we will be repackaging the toy after adapting).

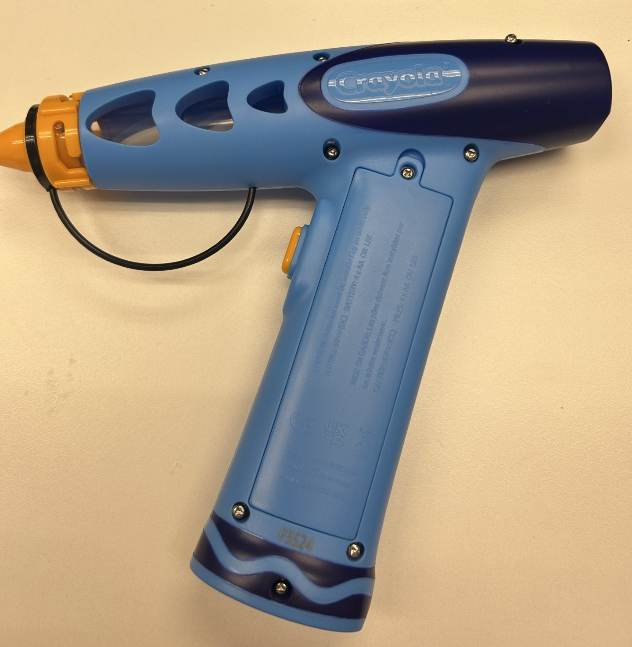
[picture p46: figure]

2. Locate and remove the 8 screws along the body of the toy, using the triangle screwdriver. Carefully separate the two halves of the toy. *Note: keep screws, and keep track of where they came from if there are multiple different sized screws

A person using a ruler to measure the length of a wire

3. Cut 2 pieces of wire, each 15 cm long.

A wire stripper removing the insulation from a wire.

4. Use wire strippers to strip approximately 0.5 cm off each end of the wires

A rectangular mono cable with two wires soldering onto the front two tabs

5. Solder the two wires onto the front two tabs of the mono jack.

Solder melted onto the end of an exposed wire.

6. Tin the other ends of the wires by adding a small amount of solder to each wire.

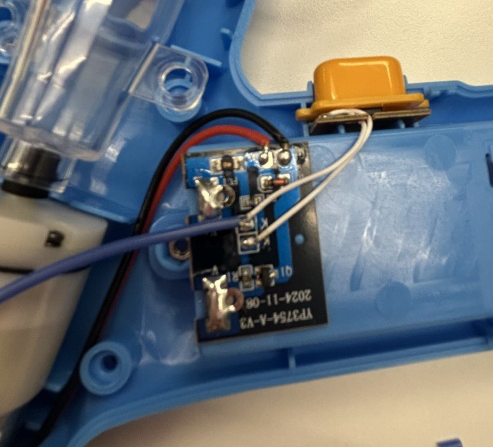
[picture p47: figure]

7. Solder the first new wire from the mono jack in parallel with the existing wire connected to the switch. Do this by carefully soldering the new wire on top of the existing wire that goes to the switch, being careful not to break the original connection.

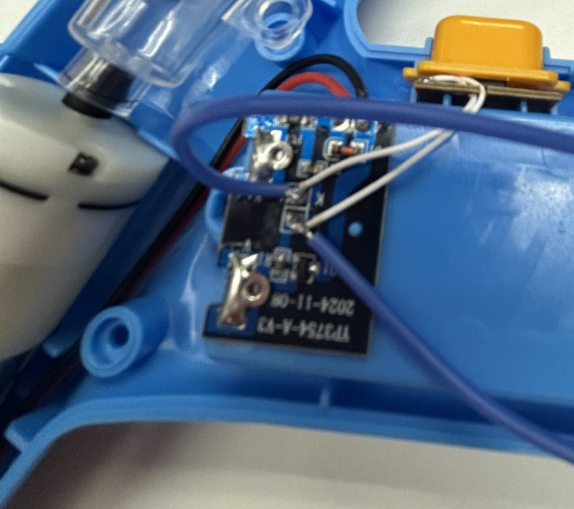
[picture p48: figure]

8. Solder the second wire from the mono jack in parallel with the existing wire. Do this by carefully soldering the new wire on top of the existing wire that goes to the switch, being careful not to break the original connection.

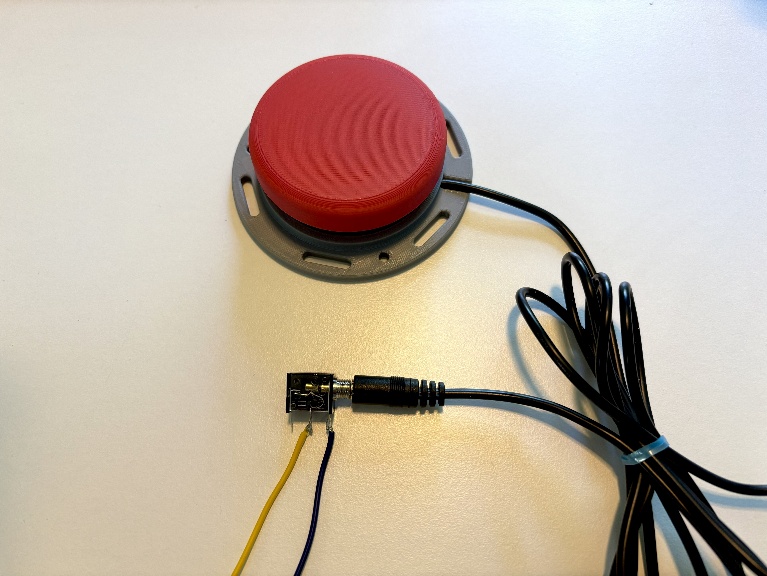
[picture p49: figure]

9. It is now time to test the toy. Insert batteries into the battery compartment and an assistive switch into the mono jack. Test to make sure that the toy can be controlled using the original switch and the assistive switch. Notes: - If the toy does not turn on, please check the soldered connections. - If the toy continuously sprays, the connection is shorted. Check for areas of touching solder and separate using a soldering iron.

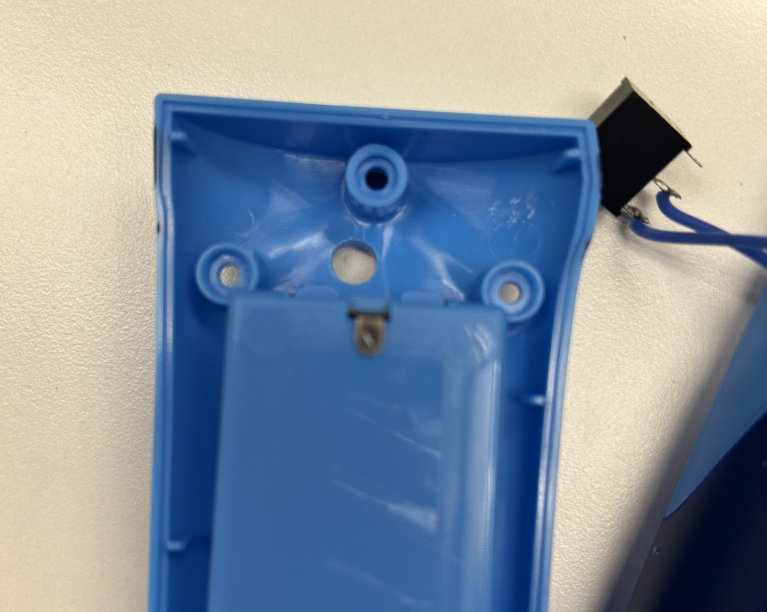
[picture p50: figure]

10. Using a ¼” drill bit, drill a hole into the position shown on the right. Remove any loose plastic.

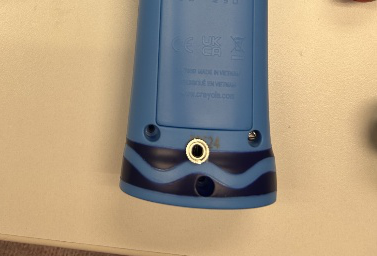
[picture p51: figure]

11. Remove the retaining ring from the mono jack and push the mono jack through the hole from the inside. Reinstall the retaining ring on the outside of the toy and tighten to secure.

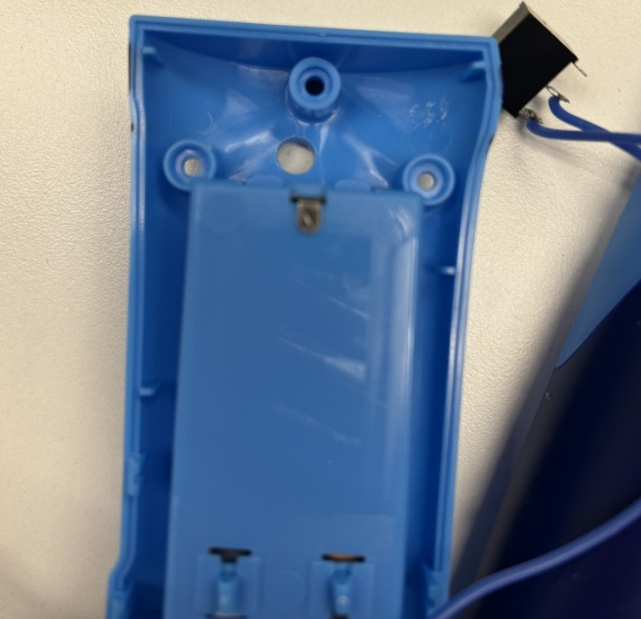
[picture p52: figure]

12. Start to reassemble the toy, tucking your new wires in along the side of the battery component.

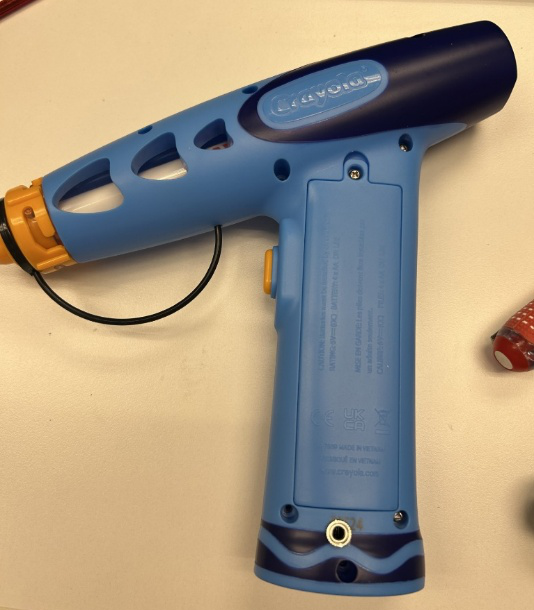
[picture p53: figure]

13. Reassemble the toy using the screws set aside earlier.

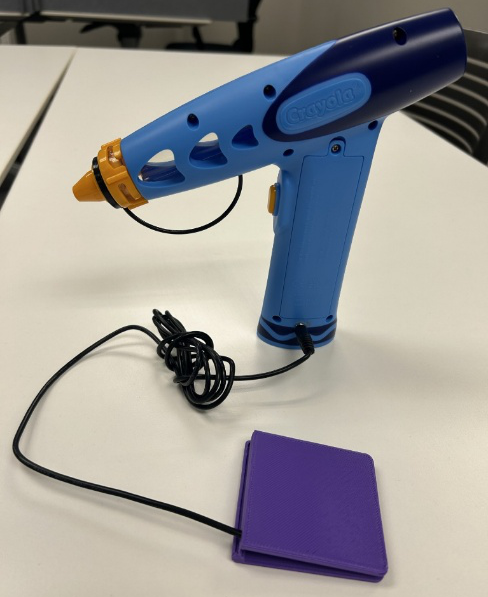
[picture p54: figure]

14. Test the toy again. If it is still working properly, repackage the toy and the adapted toy is complete!

© 2026 by Neil Squire This work is licensed under the CC BY SA 4.0 License: http://creativecommons.org/licenses/by-sa/4.0 Files available at https://github.com/makersmakingchange/Switch_Adapted_Toys Page 1 of 1

V1.0 | October 2026 Switch Adapted Crayola Marker Airbrush Spray Art Kit MAKER GUIDE

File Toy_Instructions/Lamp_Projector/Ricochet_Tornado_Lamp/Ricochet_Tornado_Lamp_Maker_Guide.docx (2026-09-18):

# Required Components

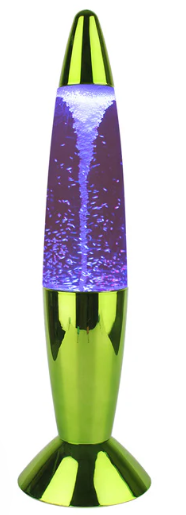
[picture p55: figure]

| 2. | BOM 1. Tornado Lamp (Canadian Tire) 2. 3.5 mm Female Mono Cable 3. Cable Tie 4. 3 AA batteries (included) Refer to the Tool and Component List (https://www.makersmakingchange.com/toy-adapting-components-and-tools) for purchasing details.

A cable tie.

# Required Tools

- Screwdriver
- Soldering iron
- Wire stripper
- Flush cutter
- Drill and ¼ drill bit

# Required Personal Protective Equipment (PPE)

- Safety Glasses

# Assembly Instructions

## Step 1

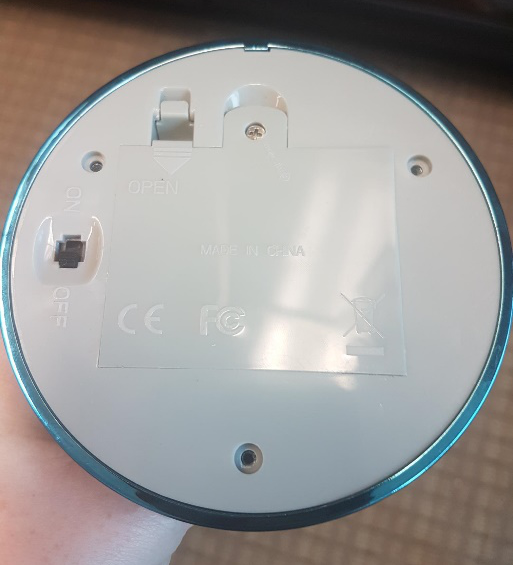
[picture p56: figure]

| - On the bottom of the lamp, locate 3 screws that hold the bottom plate in place - Using a screwdriver, turns screws indicated in the red circles to remove bottom covering - Also unscrew and take off the battery cover - Set screws aside in a safe place

## Step 2

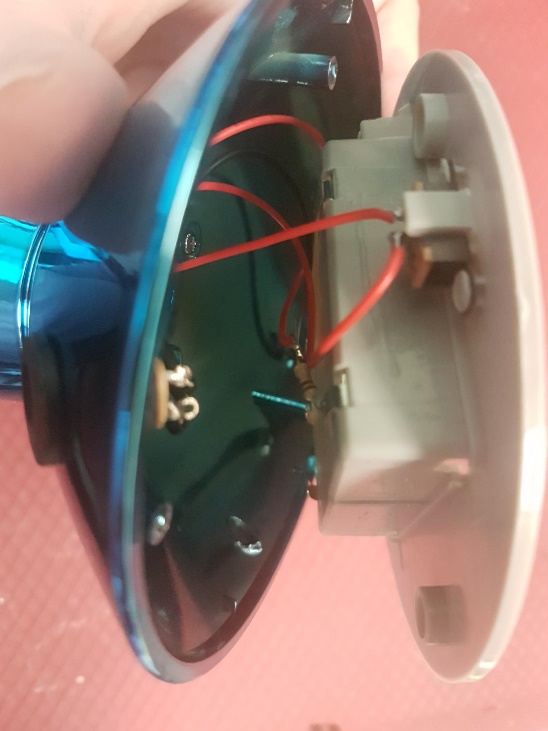
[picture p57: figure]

| - After the screws are undone, gently take the bottom of lamp off and set to the side. Be very careful while doing this as to not pull off any existing wires or connections - The wires may be short, leaving little space for the toy to be opened wide - Locate where the original on/off switch is inside the toy

## Step 3

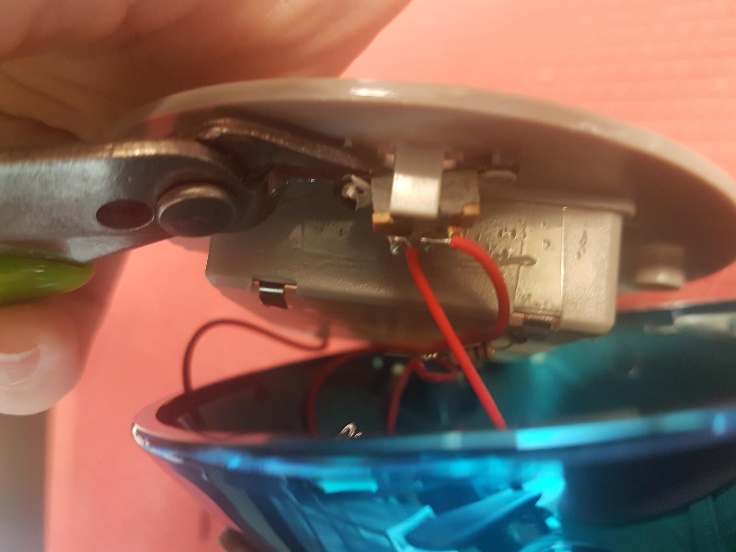
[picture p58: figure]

| - You will need to remove the original switch from the plastic holder - To do this, use your flush cutters to trim the plastic on either side of the switch - You can also use your flush cutters to wiggle or push the original switch from the plastic

## Step 4

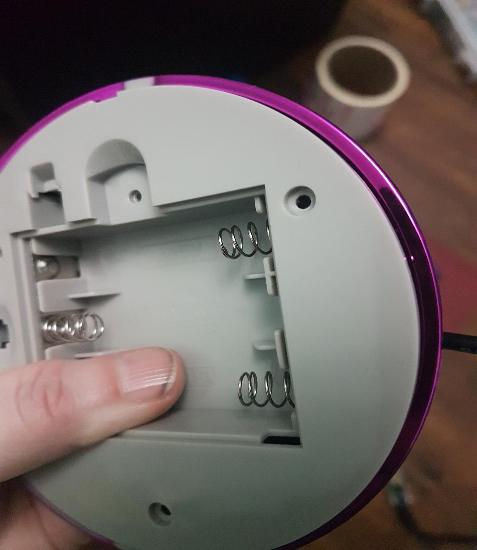
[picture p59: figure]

Cable Top of battery compartment | - Using a 1/8 drill bit, drill a hole on the side of the toy - The hole is best drilled to the right of the battery compartment, on the side of the stand - Check that the mono cable can be threaded through the hole with the exposed wires going into the toy

## Step 5

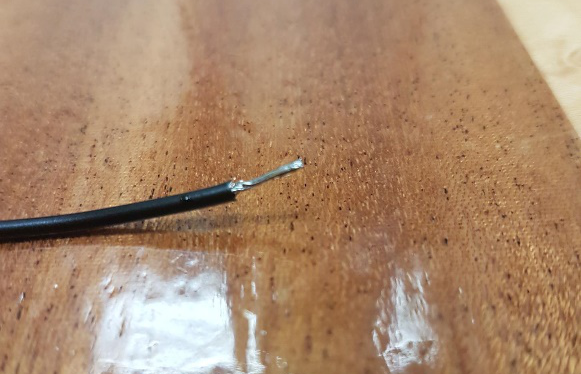
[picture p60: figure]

| - Making sure the cable is going through your drilled hole, it is now time to solder - First, you are going to “tin” the end of both of your wires, which is when you cover the exposed end of the wire in solder - This process will make it easier to solder that end of the wire to the original switch which is in the next step

## Step 6

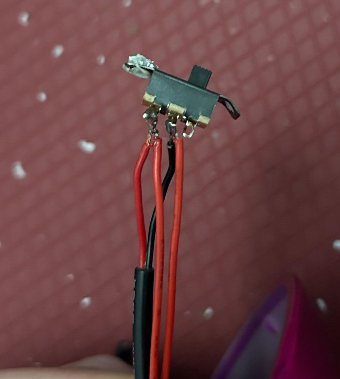
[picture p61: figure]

| - The original switch has 2 wires attached to it on 2 metal prongs - You will be attaching the wires you just prepared to this same spot: with the original wires - To do this, hold one tinned wire end to the metal prong (where there is also an original wire attached) - Then bring your solder iron to the spot with your two wire ends, and hold for about 3 seconds: this will heat the pre-existing solder of the original solder, and the solder of the wire you had just tinned, combining for one spot on the metal prong

## Step 7

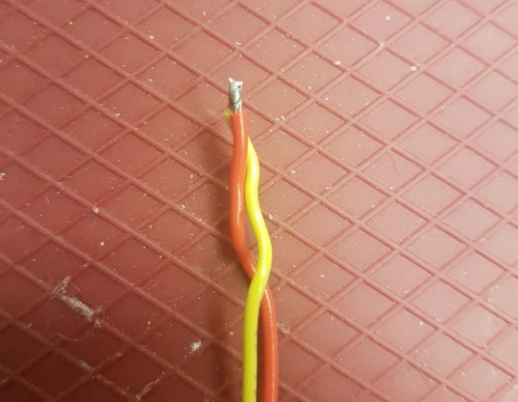
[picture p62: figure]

| - If your original wire comes loose, that is ok - You can then twist the original wire with one of the new wires and use solder to cover the two ends of wire - Then bring the wires to the metal prong, where the original wire was connected, reheat the solder so it once again sticks to the metal prong where it was originally

## Step 8

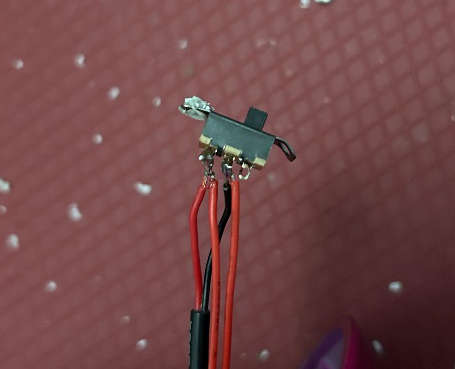
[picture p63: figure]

| - Repeat Step 6 (and Step 7 if needed) with the second wire - Make sure there is no solder going between the two metal prongs or that the wires ends are not touching - If needed, you can use electrical tape to help with separation - When complete you should have two metal prongs, each with two wires attached: one original wire and one new wire - Test the new connection using an assistive switch – you will need to add batteries

## Step 9

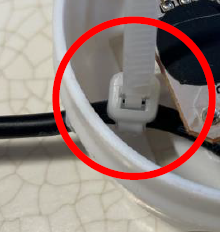
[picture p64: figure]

| - After Testing, before reassembling, add a cable tie around the cable inside of the toy - This is to help the cable from being pulled through the hole - You can snip the long end of the cable tie

## Step 10

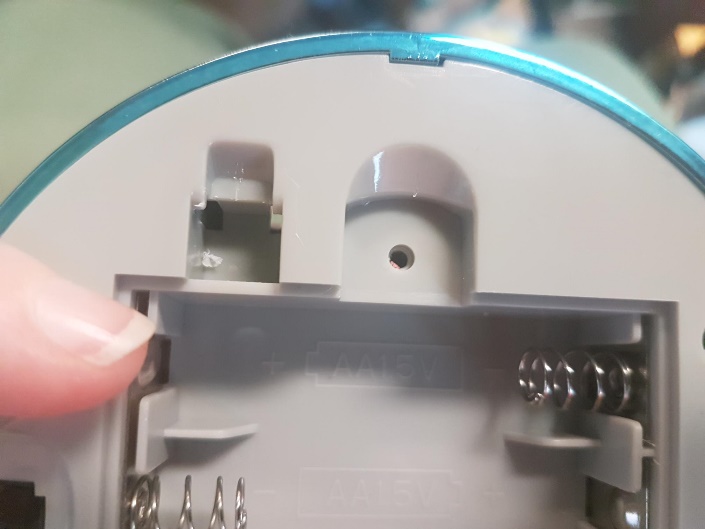
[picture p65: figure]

| - Replace the bottom of the lamp - If it is difficult to find the original position, look for the slight notch at the top to help you match the correct position - Replace and tighten the screws

## Step 11

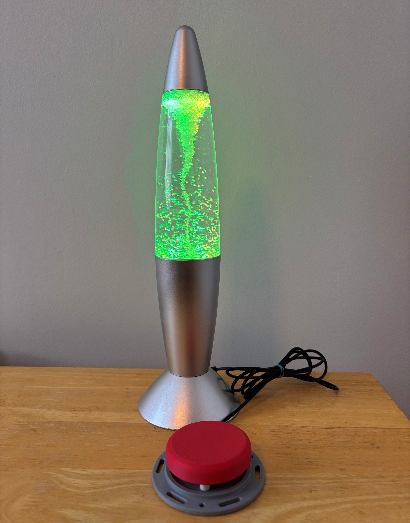
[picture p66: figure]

| - Test the toy again with an assistive switch, if it is still working properly, congratulations! You have completed the toy!

© 2023 by Makers Making Change This work is licensed under the CC BY SA 4.0 License: http://creativecommons.org/licenses/by-sa/4.0 Files available at https://github.com/makersmakingchange/Switch_Adapted_Toys Page 1 of 6

V1.1 | SEPTEMBER 2026 Tornado Lamp Assembly Guide

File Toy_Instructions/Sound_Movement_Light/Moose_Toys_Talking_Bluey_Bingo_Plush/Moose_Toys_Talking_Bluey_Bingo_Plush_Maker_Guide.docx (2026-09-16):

# Required Components


| | BOM 1. Moose Toys - Talking Bluey or Bingo Plush Toy (Bluey – Amazon (https://www.amazon.ca/dp/B08S34YH92?previewDohEventScheduleTesting=C)) 2. 7” cable with 3.5 mm jack (female) end 3. Cable tie (small – around 15 cm) 4. Cable tie (large – around 35 cm) Refer to the Tool and Component List (https://www.makersmakingchange.com/toy-adapting-components-and-tools) for purchasing details.


# Required Tools

- Phillips Head Screwdriver
- Wire strippers
- Flush cutters
- Soldering iron and solder
- Drill and 1/8” drill bit

# Required Personal Protective Equipment (PPE)

- Safety glasses

# Assembly Instructions


1. To start, pull the inside compartment from inside the toy. The compartment is connected and may need to be wiggled a bit to be pulled free 2. Locate the original cable tie. It will be in the seam of the fabric going around the plastic compartment. 3. Find an opening (you may have to snip a bit of fabric) to then snip the cable tie. When this happens, the plastic will be free from the fabric


4. Locate the screws on the back of the compartment and unscrew them to reveal the internal circuit board. Gently open compartment.


5. Using a 1/8 inch drill bit, you will drill a hole for your mono cable. The mono cable will be threaded through the hole and then soldered onto the board, so this needs to be done before soldering. The hole will be drilled into the side of the plastic compartment, the larger “bottom” part to the right side of the original large plastic button.


6. Next you will prepare your mono cable by tinning your wire. The best way to do this is cover the exposed wire in solder. You will use your soldering iron and melt solder onto the exposed wire end and this will help you solder onto the board. Thread your cable through the hole you drilled.


7. The circuit board has a grey, silicone square. For this toy, a plastic button pushes the silicone square onto the circuit board and activates the toy. Under this, are the spots you will solder your wires.


8. You can take the silicone square completely off or pull one corner up and tape to the side to access the board underneath. Now you will see silver circle with a zig zag and two very small circles next to it. The small circles are indicated in red.


9. You will be connecting your wires to the small circles, one wire soldered to each spot. To do this, you can gently add solder to the board. On each circle, add a small blob of solder. This will give you a spot to connect the wire to.


10. To connect the wires, touch one of the tinned wires from your cable to your new solder blob. Use your soldering iron to heat up the solder blob and the solder on your wire. This should allow for the wire to stick to that spot on the board. 11. Repeat with your other wire onto the other blob. Please note: It does not matter which wire is connected to which spot on the board.


12. Before we reassemble, you can test the toy by plugging a switch into the cable. When the switch is activated, Bluey will talk. If there any issues, check the connections and that solder is not on any spots of the board it should not be. 13. Next attach your small cable tie around the cable on the inside of the plastic compartment. This is to help with the cable from being pulled back through the hole.


14. You can now prepare to close the compartment. If possible, you can put the grey silicone square back on the board, however this may be difficult as the new wires may be in the way. Add the plastic button back into the compartment, it will no longer activate Bluey if the silicone is not there which is alright as we will now be activating the toy by cable.


15. Add the screws and close the plastic compartment. 16. Locate your large cable tie and thread it through the seam in the fabric. Add the compartment back into the fabric and notice the ridge on the plastic compartment which the cable tie will go around. When the compartment and fabric is in place, tighten the cable tie so it is secure.


17. Put the compartment back inside Bluey and close the Velcro, except for the cable. The cable should be hanging out the back so a switch can be attached for use. 18. If possible, put Bluey back into its original box and seal – toy is complete!

© 2022 by Makers Making Change. This work is licensed under the CC BY SA 4.0 License: http://creativecommons.org/licenses/by-sa/4.0 Page 1 of 2

V1.0 | November 2024 Switch Adapted Talking Bluey Plush Toy Assembly Guide

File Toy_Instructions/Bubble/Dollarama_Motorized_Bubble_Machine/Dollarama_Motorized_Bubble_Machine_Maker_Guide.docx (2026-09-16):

# Required Components


| | BOM 1. Dollarama – Motorized Bubble Machine (Hippo or Frog) 2. 3.5 mm Mono Jack and Nut 3. 22 AWG Wire 4. 2 AA Batteries Refer to the Tool and Component List (https://www.makersmakingchange.com/toy-adapting-components-and-tools) for purchasing details.


# Required Tools

- Philips head screwdriver
- Ruler
- Flush cutters
- Wire strippers
- Soldering iron and solder
- Drill and 1/4” drill bit

# Required Personal Protective Equipment (PPE)

- Safety glasses

# Assembly Instructions


1. Carefully remove the toy from its packaging without damaging it. Locate and remove the six screws along the body of the toy and keep in a safe place.


2. Carefully separate the two halves of the toy and set aside the front half.


3. Cut 2 pieces of wire, each approximately 8cm long.


4. Use wire strippers to strip approximately 0.5cm off each end of the wires.


5. Solder the two wires onto the two legs of the jack closest to the mono jack hole.


6. Tin the other ends of the wires by placing a small amount of solder on each wire.


7. Solder the new wires in parallel with the existing red wires that connect to the switch. Do this by carefully soldering the new wires on top of the red wires, one at a time.


8. It is now time to test the toy. Insert 2 AA batteries into the battery compartment and insert an assistive switch into the mono jack. When the switch is pressed, the toy will turn on and you can move onto the next step. You should also still be able to control the toy with the original switch. Note: If the toy does not turn on, please check the soldered connections.


9. Using a ¼” drill bit, drill a hole into the back of the toy, near the original switch. Cut away any loose plastic.


10. Remove the nut from the mono jack and push the mono jack through the hole from the inside. Reinstall the nut on the outside of the toy and tighten to secure.


11. Reassemble the toy using the 6 screws from earlier.


12. Test the toy again. If it is still working properly, remove the batteries, repackage the toy and the adapted toy is complete!

© 2026 by Makers Making Change This work is licensed under the CC BY SA 4.0 License: http://creativecommons.org/licenses/by-sa/4.0 Files available at https://github.com/makersmakingchange/Switch_Adapted_Toys Page 1 of 6

V1.0 | July 2025 Switch Adapted Motorized Bubble Machine MAKER GUIDE

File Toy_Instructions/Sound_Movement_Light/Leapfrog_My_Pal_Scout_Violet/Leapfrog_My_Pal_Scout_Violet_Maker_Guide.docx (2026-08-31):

# Required Components

A green and white stuffed animal in a box

| | BOM 1. Leap Frog My Pal Scout or Violet Smarty Paws (Walmart Scout (https://www.walmart.ca/en/ip/LeapFrog-My-Pal-Scout-Smarty-Paws-Personalized-Plush-Puppy-English-Version/3B87UQPQ4KFM), Walmart Violet (https://www.walmart.ca/en/ip/LeapFrog-My-Pal-Violet-Smarty-Paws-Personalized-Plush-Puppy-English-Version/7CU457U03CMA), Amazon Scout (https://www.amazon.ca/LeapFrog-Personalization-lullabies-Learning-Content/dp/B09VN13PFG), Amazon Violet (https://www.amazon.ca/dp/B09VNXXGC5?th=1), Amazon Scout French (https://www.amazon.ca/LeapFrog-Personalization-lullabies-Learning-Content/dp/B09VNG6KLY)) 2.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

A black cable tie with a black strap
A black cable tie with a black strap
Prime-Line 9018921 Sheet Metal Screw, Self-Tapping, Pan Head Phillips, 4 X 3/8 in, Grade 18-8 Stainless Steel, Pack of 25

# Required Tools

- Phillip screwdriver
- Wire strippers
- Flush cutters
- Soldering iron and solder
- Scissors

# Required Personal Protective Equipment (PPE)

- Safety glasses

# Assembly Instructions


1. Open the toy carefully by cutting the toy out of the packaging.


2. Once the toy has been removed open the Velcro on the back of the toy and pull out the white internal casing.


3. Near the bottom of the case by the printed “Item No.”, carefully tear the fabric by 1cm to expose the cable tie underneath. Cut off the cable tie knot to release the casing from the fabric. Pull the cable tie out as this is now garbage.


4. Each switch on the toy will have two wires leading to it, and the switches are in the ears and feet of the toy. To determine which wire goes to which switch, you can trace the wires from the plastic case to the switch to which they are connected. The ears and feet have images which represent what each switch does when pressed. Note: wire colours will be different on all toys. Trace the wires to each paw to keep track of which wires are responsible for each feature Note: There are extra wires that will not be used in this toy adaptation


5. Working with one wire at a time, cut through the middle of the wire and strip 3 cm off each end. Note: It is important to follow steps 6-10 one wire at a time to avoid mixing up the wires and switches.


6. Take your two newly stripped wires and one of the wires from the female cable and twist the three wire ends together. Note: Some of the female cables come pre-stripped others may not. Strip the insulation from the ends of the female cable wires if necessary.


7. Solder the three wires together.


8. Repeat steps 6-8 to the other wire going to the same switch, and the other female jack wire.
9. Stop and test with an adaptive switch. Label the female mono jack with tape and a marker to easily keep track of each function
10. Repeat steps 6 – 10 for the three other remaining jacks.


11. Wrap the exposed, soldered cables in electrical tape.


12. Once all cables have been tested and wrapped in electrical tape, we are ready to re-assemble.


13. Place all the wires back inside the belly of the toy. Pull the female audio leads through to the outside and using the new cable tie, “reseal” the casing back into the fabric of the plushy. There will be a hole to feed the cable tie through the spot of the one we cut away to get into the toy. Once the cable tie has been tightened. Cut off the excess end of the cable tie and tuck the head of the cable tie into the fabric.


14. Secure the audio cables in the cable clamp, ensuring the jacks go in their corresponding spots based on the images that match the images on the toy’s paws. This can be done using a switch to test each jack and pushing on the buttons in the paws to compare.


15. Secure the four cables with the 4’’ cable tie directly above the 3D printed cable clamp
16. Test the toy again, and ensure each cable matches the symbol on the 3D printed cable clamp


17. Repackage the toy in the original box

© 2025 by Makers Making Change. This work is licensed under the CC BY SA 4.0 License: http://creativecommons.org/licenses/by-sa/4.0 Page 1 of 2

V1.0 | August 2026 Switch Adapted My Pal Scout and Violet maker Guide

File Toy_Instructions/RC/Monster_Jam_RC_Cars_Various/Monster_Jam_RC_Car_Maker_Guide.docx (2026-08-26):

## Required Components

A box of remote control monster truck

1. or or | 2. | BOM 1. Monster Jam RC Car, multiple varieties. Either: El Toro Loco (https://www.amazon.ca/Monster-Jam-Official-Remote-Control/dp/B08FCRT7WC), Megalodon (https://www.amazon.ca/Monster-Jam-6047110-Official-Megalodon/dp/B07HGTJBGJ?th=1), or Marvel Iron Man (https://www.amazon.ca/Monster-Jam-Marvel-Iron-Truck/dp/B0CSFNYC8M?th=1) 2. (4x) 3.5 mm Female Mono Cable 3. 3D Printed Cable Clamp 4. (2x) #4 3/8” screws 5. (5x) AAA batteries Refer to the Tool and Component List (https://www.makersmakingchange.com/toy-adapting-components-and-tools) for purchasing details.

A black rectangular 3D printed object with white arrows
A close-up of a screw
A close-up of a screw

3. | 4. | 5.

## Required Tools

- Phillips Screwdriver
- Wire strippers
- Soldering iron and solder
- Drill and 1/8” drill bit

## Required Personal Protective Equipment (PPE)

- Safety glasses

## Assembly Instructions


1. Carefully remove the toy from its packaging without damaging it (we will be repackaging the toy after adapting). Locate and remove the 2 screws on the back of the remote control.

The inside of the remote control. A blue PCB board with electrical components

2. Carefully separate the two halves of the remote and remove the joystick toppers.

A black mono cable on a white surface

3. To prepare the mono cable, use wire strippers to strip approximately 2 cm off the outer wire casing, revealing two internal wires. Repeat for all four mono cables. Note: your mono cables may come prepped and ready to solder, with both wires revealed and metal on the ends exposed (skip steps 3-5).

A black wire with a wire stripper

4. If there are 2 internal wires, strip approximately 0.5 cm off each wire.

A wire with three internal wires showing at the end
A black wire with two internal wires at the end.

5. If there are three internal wires (red, black, and exposed), strip off 0.5 cm of the red insulation and twist the red wire and exposed wire together. Strip 0.5 cm from the black wire.

A black wire on a wood surface. The end of the wire is silver and coated in solder.

6. Melt a small amount of solder over the exposed ends of the wire.


7. Using a 1/8” drill bit, drill 4 holes into the positions shown on the right. Remove any loose plastic.

8. Insert the mono cables through the holes.  For each mono cable solder the two leads to the two matching circles shown on the image. Make sure to not get solder on a prong that is not meant to be soldered.

A close up of the blue PCB showing a red and black wire soldered to two diagonal joints on the bottom left button.

9. This is what the soldered mono cable will look like.

A hand holding a small rectangular switch. The open remote control is shown in the backround with wires around.

10. After finishing each mono cable, test it. Insert the batteries into the remote and car and turn the car on. Plug in an assistive switch. When you activate the switch, the car will perform the function of the button you soldered the cable to (Forward, Backward, Left, Right). If the car does not move, make sure the batteries are pressed in fully and check the solder connections. If the car does not stop moving when you release the switch, check the solder connections.

The open remote control with the blue PCB. Two wires are soldered to each of the four buttons on the PCB.

11. When you have soldered all four cables, the PCB will look like this:

The open remote control with the two joysticks placed over the PCB. Four wires are coming out of the remote control, and are gathered at the bottom. They are placed in a small rectangular object that is the bottom of the 3D printed cable clamp.
The top of the cable clamp is placed over the wires. There are four white arrows on this part.
Back view of the cable clamp with a black screw inserted on each end.

12. Gather the mono cables, and put the cable clamp on, ensuring that each wire is lined up with the proper symbol on the clamp. Insert the screws into the two holes on the back, and tighten to fasten the cable clamp.

The open remote control with the joystick toppers placed in their locations along the middle of the PCB.

13. Place the joystick toppers back on.

The black remote control with four wires sticking out.

14. Close the remote control and insert the two screws back into the remote.

The black remote control with four wires coming out, gathered by a rectangular cable clamp with four white arrows on it. A hand is holding a green assistive switch that is plugged into one of the cables.

15. Test the toy again. If it is still working properly, repackage the toy and the adapted toy is complete!

© 2026 by Makers Making Change This work is licensed under the CC BY SA 4.0 License: http://creativecommons.org/licenses/by-sa/4.0 Page 1 of 1

V1.0 | May 2026 Switch Adapted Monster Jam RC Car MAKER GUIDE

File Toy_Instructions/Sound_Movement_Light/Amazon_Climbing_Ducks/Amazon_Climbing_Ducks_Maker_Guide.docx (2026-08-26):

# Required Components


| | BOM 1. Amazon (https://www.amazon.ca/Climbing-Electric-Llittle-Coaster-Toddlers/dp/B0DGGWF565?th=1) LED Electric Duck Climbing Stairs Toy 2. Mono jacks x2 3. 22 AWG Wire 4. 2 AA Batteries Refer to the Tool and Component List (https://www.makersmakingchange.com/toy-adapting-components-and-tools) for purchasing details.


# Required Tools

- Phillips Screwdriver
- Soldering iron
- Wire stripper
- Flush cutter
- Drill and ¼ drill bit

# Required Personal Protective Equipment (PPE)

- Safety Glasses

# Assembly Instructions

## Step 1


| - Carefully remove toy from packaging, the toy will be put back in packaging (if possible) after it is adapted - This toy has a lot of parts – ducks and a track that can be kept in the box - Using a screwdriver, turns screws indicated in the red circles to open the toy – including the screw inside the batter compartment - Set screws aside in a safe place

## Step 2


| - After screws are undone, gently pull the toy into two halves. Be very careful while doing this as to not pull off any existing wires or connections - If some parts move, just take note of how everything fits together but they can also be set aside while you work on the toy.

## Step 3


| Next we will prepare the mono jack and wires. Cut 2 pieces of wire each 8 cms in length Strip both ends of both wires, leaving about .5 cm of exposed wire on each end

## Step 4


| - Pick one wire, slide exposed wire into first metal arm on mono jack (the arm closest to the circular jack) - With second wire, slide one end of exposed wire into the middle metal arm on mono jack - Solder wire to mono jack Please Note: Check that you have the correct metal arms of mono jack, refer to picture

## Step 5


| - Tin the ends of your wire. The best way to do this is cover the exposed wire end in solder. - This will help you stick the wires to an existing spot where the is solder

## Step 6


| - Locate where the on/off switch is located. Undo the screws and gently pull the switch to give yourself space to work with it - For this assembly, we are attaching our mono jack + wires to the same spots on the original switch

## Step 7


| - Using the wires and mono jack you previously prepared, you will solder the ends of your new wire to where the current red wires are. - You will have one new wire and one old wire coming from each spot indicated in the circles - Test your connections using an assistive switch. Listen for the motor to start when the switch is activated. Please note: you will need batteries to test

## Step 8


| - Using a ¼ inch drill bit, drill a hole to the side of the battery compartment. - Check that the mono jack end fits through the hole and that it does not interfere with any mechanism of the toy. - Add the ring to the outside of the toy to hold the mono jack in place.

## Step 9


| - Reassemble the original switch to its original position, close the toy – checking that no wires are being pinched and the mechanics are moving. - Reassemble by adding the screws to their original spots. Test the toy again once reassembled.

© 2023 by C Cameron – Makers Making Change. This work is licensed under the CC BY SA 4.0 License: http://creativecommons.org/licenses/by-sa/4.0 Page 1 of 1

V1.1 | August 2026 Switch Adapted Climbing Ducks Toy MAKER Guide

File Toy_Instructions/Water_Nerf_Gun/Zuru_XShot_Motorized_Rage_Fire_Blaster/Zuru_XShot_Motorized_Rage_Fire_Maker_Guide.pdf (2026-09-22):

V1.0.0 | SEPTEMBER 2026

## Switch Adapted Zuru XShot Motorized Rage Fire

## MAKER GUIDE

© 2026 by Makers Making Change, Neil Squire. This work is licensed under the CC BY SA 4.0 License: http://creativecommons.org/licenses/by-sa/4.0
Files available at https://github.com/makersmakingchange/Switch_Adapted_Toys | Page 1 of 10

### Required Components


1. | 2. | BOM
1. Zuru XSHOT Motorized Rage Fire
| | (Walmart, (https://www.walmart.ca/en/ip/XSHOT-Insanity-Motorized-Rage-Fire-72-Darts-by-ZURU/6000207153516) Amazon, (https://www.amazon.ca/Insanity-Motorized-Technology-Storage-Blasting/dp/B0BS4CDB59) Canadian Tire) (https://www.canadiantire.ca/en/pdp/x-shot-insanity-s1-motorised-rage-fire-dart-blaster-ages-8-1500754p.html)
2. (2x) 3.5 mm Mono Jack and Ring
3. 22 AWG Wire
4. (6x) AA Batteries


5. Toggle switch (https://www.amazon.ca/dp/B07QC6TTD8?ref=fed_asin_title)
| | Refer to the Tool and Component List (https://www.makersmakingchange.com/toy-adapting-components-and-tools) for purchasing details.


3. | 4. | 5.

### Required Tools

- Small Phillips Screwdriver 3mm Diameter
- Ruler
- Wire strippers
- Soldering iron and solder
- Drill and 1/4” drill bit

### Required Personal Protective Equipment (PPE)

- Safety glasses

## Rage Fire

## MAKER GUIDE

© 2026 by Makers Making Change, Neil Squire.

Files available at https://github.com/makersmakingchange/Switch_Adapted_Toys | Page 2 of 10

### Assembly Instructions

1. Carefully remove the toy from its packaging without damaging it (we will be repackaging the toy after adapting). Carefully open up the cardboard, and then on the backside of the toy, twist off the plastic pieces holding the toy to the cardboard (shown circled in the photo).
2. Remove the two screws from inside the handle at the top of the toy, shown circled here, then remove the handle. *Note: keep screws, and make sure not to lose them

## Rage Fire

## MAKER GUIDE


© 2026 by Makers Making Change, Neil Squire.

Files available at https://github.com/makersmakingchange/Switch_Adapted_Toys | Page 3 of 10
3. Locate and remove the 20 screws along the body of the toy.

*Note: keep screws, and make sure not to lose them

4. Carefully separate the two halves of the toy, making note of any pieces that move or fall out.
5. Cut 6 pieces of wire, each 12 cm long.

## Rage Fire

## MAKER GUIDE


© 2026 by Makers Making Change, Neil Squire.

Files available at https://github.com/makersmakingchange/Switch_Adapted_Toys | Page 4 of 10
6. Use wire strippers to strip approximately 0.5 cm off each end of the wires
7. Solder two of the wires onto the front two tabs of the first mono jack, closest to the jack input. Repeat with the second mono jack.
8. Solder two of the wires onto the left and middle tabs of the toggle switch.

## Rage Fire

## MAKER GUIDE

9. Take one wire from the toggle switch and one wire from one of the mono jacks and twist the ends of the wires together and solder them. Then repeat with the remaining two wires.; 10. On the other mono jack (that is not soldered to the toggle switch), tin the other ends of the wires by adding a small amount of solder to each wire.; that are soldered together and solder; the positions shown (the two legs furthest from the switch). Do this by carefully soldering the new; careful not to break the original connection. Each of the two solder; wire, the mono jack, and the toggle switch.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

© 2026 by Makers Making Change, Neil Squire.

Files available at https://github.com/makersmakingchange/Switch_Adapted_Toys | Page 5 of 10
11. Take the mono jack and toggle switch

them in parallel with the existing wires connected to the switch on the right, in

wires on top of the existing wires, being

joints will now have 3 wires: the original

Note: if it is easier, you can carefully lift/pry the switch out of the plastic enclosure (as

## Rage Fire

## MAKER GUIDE

© 2026 by Makers Making Change, Neil Squire.

Files available at https://github.com/makersmakingchange/Switch_Adapted_Toys | Page 6 of 10
12. Next, take the other mono jack and solder it in parallel with the existing wires connected to the switch on the left, in the positions shown (the two legs furthest from the switch). Do this by carefully soldering the new wires on top of the existing wires, being careful not to break the original connection. Each of the two solder joints will now have 2 wires: the original wire and the mono jack.
13. Once all connections have been soldered, it should look something like this photo, with the switch on the left soldered to a mono jack, and the jack on the right soldered to both a mono jack and the toggle switch.
14. It is now time to test the toy. Insert batteries into the battery compartment and assistive switches into the mono jacks. Test to make sure that the toy can be controlled using the original switch, the assistive switches, and the toggle switch. Do not use foam darts while testing, just listen for the motor. Notes:
- The toggle switch and the mono jack connected to the switch on the right both control the “charge up” motor. You will hear the motor but will not see things move. Test these one at a time.
- The mono jack connected to the switch on the right should control the “shoot” function, the barrel at the front of the blaster will spin and the wheel that feeds the darts will also spin.

## Rage Fire

## MAKER GUIDE

Troubleshooting:; activation methods, please check the soldered connections. - If the toy does not turn off when the; switch is turned off, the connection is; and separate using a soldering iron.; positions shown on the right. Remove any loose plastic.; of the nuts and then the washer with a small tab on it (shown below), with the tab angled down or towards the wires, as shown on the right.

© 2026 by Makers Making Change, Neil Squire.

Files available at https://github.com/makersmakingchange/Switch_Adapted_Toys | Page 7 of 10
- If the toy does not turn on, with any of the

assistive switch is released and the toggle

shorted. Check for areas of touching solder

15. Using a ¼” drill bit, drill 3 holes in the
16. Take the toggle switch and put on one

## Rage Fire

## MAKER GUIDE


© 2026 by Makers Making Change, Neil Squire.


Files available at https://github.com/makersmakingchange/Switch_Adapted_Toys | Page 8 of 10
17. Put the toggle switch through the upper left hole. Then from the outside of the toy, add the other washer with barbs and the second nut (shown below).
18. Now, take the mono jack that is soldered to the right switch, the same switch as the toggle switch. If the retaining ring is on the jack, remove it and push the mono jack through the hole beside the toggle switch from the inside. Reinstall the retaining ring on the outside of the toy and tighten to secure.

## Rage Fire

## MAKER GUIDE

and push the mono jack through the bottom hole from the inside. Reinstall; toy and tighten to secure.; 20. Now we are going to reassemble the; moved or fell out when taking the toy apart.; The trigger piece will need to be put back into place, with the spring on the end of the part and on the blue post nearby, as shown.; Check for any other pieces that may have fallen out or out of place, by referencing the second photo shown here.

© 2026 by Makers Making Change, Neil Squire.

Files available at https://github.com/makersmakingchange/Switch_Adapted_Toys | Page 9 of 10
19. Take the remaining mono jack, if the retaining ring is on the jack, remove it

the retaining ring on the outside of the

toy, start by reinstalling any pieces that

## Rage Fire

## MAKER GUIDE

toy back together, making sure everything is lined up as you do so. In particular, make sure the part shown in this photo is lined up with the hole on the other side, as this can be tricky. 22. Once the two halves are together, reassemble the toy using the screws set aside earlier.; 23. Now, reassemble and reinstall the; orange part through the orange hole on; then take the other half of the handle and insert it into both the hole on the; Screw the two screws back in.; time. Always turn on the toggle switch OR press the “charge up” assistive switch next to the toggle switch before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

© 2026 by Makers Making Change, Neil Squire.

Files available at https://github.com/makersmakingchange/Switch_Adapted_Toys | Page 10 of 10
21. Now, carefully put the two halves of the

handle to the top of the toy. Put the half of the handle that is still attached to the

the top of the toy (circled in the photo),

blaster and the other half of the handle.

24. Test the toy again. If it is still working properly, test again with the darts this

pressing the “shoot” switch. If it shoots

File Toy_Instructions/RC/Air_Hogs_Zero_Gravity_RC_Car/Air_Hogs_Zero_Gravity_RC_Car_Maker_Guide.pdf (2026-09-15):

V1.1 | SEPTEMBER 2026

## Switch Adapted Air Hogs Zero Gravity RC Car

## MAKER GUIDE


© 2026 by Makers Making Change This work is licensed under the CC BY SA 4.0 License: http://creativecommons.org/licenses/by-sa/4.0
Files available at https://github.com/makersmakingchange/Switch_Adapted_Toys | Page 1 of 6

### Required Components

1. | 2. | BOM 1. Air Hogs Zero Gravity Sprint RC Car (https://www.amazon.ca/dp/B0BRT9C5S2?ref=fed_asin_title&th=1) 2. (4x) 3.5 mm Female Mono Cable 3. 3D Printed Cable Clamp 4. (2x) #4 3/8” Screws 5. (4x) Mini cable ties 6. (2x) AAA Batteries Refer to the Tool and Component List (https://github.com/makersmakingchange/Switch_Adapted_Toys/blob/main/Resources/Switch_Adapted_Toys_Component_and_Tool_List.pdf) for purchasing details.
3. | 4. | 5.

6.

### Required Tools

- Small Phillips Screwdriver 3mm Diameter
- Wire strippers
- Soldering iron and solder
- Drill and 1/8” drill bit

### Required Personal Protective Equipment (PPE)

- Safety glasses

## MAKER GUIDE

1. Carefully remove the car and controller from its packaging without damaging it (we will be repackaging the toy after adapting). Locate and remove the screws along the body of the controller.; *Note: keep screws in a safe place

© 2026 by Makers Making Change

Files available at https://github.com/makersmakingchange/Switch_Adapted_Toys | Page 2 of 6

### Assembly Instructions

2. Carefully separate the two halves of the toy.
3. To prepare the mono cable, use wire strippers. Strip enough outer wire sheathing to leave two 35 mm wires protruding. Repeat for all four mono cables.
4. If there are 2 internal wires, strip approximately 3 mm or 1/8” off each wire.

## MAKER GUIDE

need to determine which wire is “Tip” “Ring” and “Sleeve”. The most common wire colours are white (Tip), red (Ring) and green (Sleeve). If there is no White wire, then “Tip” may be black. If there is no green wire, the sleeve may be an UNCOATED silver or copper colour. As cable wire colours can vary, have the wires tested with a multimeter if unsure. Once you have determined which wire is which, strip off 3 mm from the end of each wire, and solder together the “Ring” and “Sleeve” wires, as shown here.

© 2026 by Makers Making Change

Files available at https://github.com/makersmakingchange/Switch_Adapted_Toys | Page 3 of 6
5. If there are 3 internal wires, you’ll
6. Tin the ends of the wires by adding a small amount of solder to each wire.
7. Using a 1/8” drill bit, drill 4 holes in the top half of the case into the positions shown on the right (See next panel for example). Remove any loose plastic.

## MAKER GUIDE

© 2026 by Makers Making Change

Files available at https://github.com/makersmakingchange/Switch_Adapted_Toys | Page 4 of 6
8. Insert the mono cables through the holes.
9. Solder the upper left case wires to the two contacts on the upper left switch, shown circled. Solder the lower left case wires to the two contacts on the lower left switch, shown circled. When you’ve soldered both left cables, the PCB should look like this:
10. Solder the upper right case wires to the two contacts on the rightmost switch, shown circled on the right. Solder the lower right case wire to the two contacts on the adjacent switch to its left, shown in the left circle. When you’ve soldered the two right-side cables, the PCB should look like this:

## MAKER GUIDE

© 2026 by Makers Making Change


Files available at https://github.com/makersmakingchange/Switch_Adapted_Toys | Page 5 of 6
11. Next, test the toy. Make sure both the remote and car have batteries inserted and that the car is turned on. Plug in an assistive switch. When you activate the switch, the car should perform the function of the button you soldered the cable to (Forward, Backward, Left, Right). If the car does not move, make sure the batteries are pressed in fully and check the solder connections. If the car does not stop moving when you release the switch, check the solder connections. Repeat this for each cable.
12. Once the wires are connected, attach cable ties to the cable on the inside of the case as close as possible to where it enters. Tighten the cable tie as much as you can and snip the excess cable tie. Leaving 3mm of strap on cable ties allows re-tightening with needle nose pliers. The cable ties will serve as strain relief, so the soldered connections do not get pulled and break.
13. Begin reassembling the case. Pull the four cables out until they're stopped by the cable ties. Gently nestle down the lid while ensuring the wires don’t get pinched under the black button presser panel, or any of the posts.

## MAKER GUIDE

© 2026 by Makers Making Change


Files available at https://github.com/makersmakingchange/Switch_Adapted_Toys | Page 6 of 6
14. Reassemble the toy using the screws set aside earlier.
15. Gather the mono cables, and put the cable clamp on, ensuring that each wire is lined up with the proper symbol on the clamp. Insert the screws into the four holes on the back, and tighten to fasten the cable clamp.
16. Test each cable of the toy again. If it is not working properly, take apart the controller and ensure that none of the wires were pinched while assembling the controller. If it still doesn’t work, check the soldered connections.

If it is still working properly, repackage the toy and the adapted toy is complete!

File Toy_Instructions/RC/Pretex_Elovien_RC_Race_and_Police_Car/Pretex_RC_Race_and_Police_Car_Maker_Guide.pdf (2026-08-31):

V1.1 | AUGUST 2026

## Switch Adapted RC Police and Race Car

## MAKER GUIDE


© 2022 by Josie Versloot – Makers Making Change. This work is licensed under the CC BY SA 4.0 License: http://creativecommons.org/licenses/by-sa/4.0
Files available at https://makersmakingchange.com/project/switch-adapted-rc-car-toy/ | Page 1 of 11

Required Components


1. | 2. | BOM
1. Prextex RC Police and Race Car
| | (Police Car, (https://www.amazon.ca/Elovien-Remote-Control-Police-Toddlers/dp/B0D93SP3NF/ref=sr_1_3_sspa?th=1) Race Car, (https://www.amazon.ca/dp/B0DJ6SV6H1/ref=sspa_dk_detail_1?th=1) Pink Car, (https://www.amazon.ca/Elovien-Remote-Control-Police-Toddlers/dp/B0D93T3QX7/ref=sr_1_3_sspa?th=1) 2 pack Police + Race Car, (https://www.amazon.ca/Remote-Control-Cartoon-Police-Racing/dp/B085HMKDKC/ref=sr_1_5) 2 pack Truck and Tractor) (https://www.amazon.ca/PREXTEX-Remote-Control-Toddler-Girls/dp/B0B15GZ37P/ref=sr_1_4?th=1)
2. 3.5mm mono jack and nut (x2)
3. 22 AWG Wire
4. 10k pF (103) capacitor (x2)
5. AA batteries (x5)
| | Refer to the Tool and Component List (https://www.makersmakingchange.com/toy-adapting-components-and-tools) for purchasing details.
3. 4.

Required Tools

- Drill with ¼” bit
- Small flat head or Phillips screwdriver
- Flush cutters
- Wire strippers
- Soldering iron and solder
- Permanent marker

Required Personal Protective Equipment (PPE)
- Safety glasses

## MAKER GUIDE


Files available at https://makersmakingchange.com/project/switch-adapted-rc-car-toy/ | Page 2 of 11

Assembly Instructions

Step 1
From the backside of the remote, remove the screw for the battery cover (red circle). Remove the other 6 screws (yellow circles). Set aside these screws in a safe spot.
Step 2
Take apart the two halves
of the remote Set aside the front half of the remote.

1

## MAKER GUIDE


Files available at https://makersmakingchange.com/project/switch-adapted-rc-car-toy/ | Page 3 of 11
Step 3
Remove screw holding down the circuit board, circled in yellow.

NOTE: set aside screw in a safe spot

Step 4
Lift the circuit board off the pegs and flip it around to show the back.

## MAKER GUIDE


Files available at https://makersmakingchange.com/project/switch-adapted-rc-car-toy/ | Page 4 of 11
Step 5
Cut 4 pieces of wire, approximately 10 cm each.
Step 6
Strip both ends of all 4 wires, approximately 0.5 cm.
Step 7
Wrap two wires on the two leads of the mono jack nearest the jack input.

Solder the wires to these leads.

Do not attach a wire to the third lead, furthest from the jack input.

Repeat for both mono jacks.

CHECK: make sure no solder or wires are connecting two of the leads of the mono jack.

3

## MAKER GUIDE


Files available at https://makersmakingchange.com/project/switch-adapted-rc-car-toy/ | Page 5 of 11
Step 8
Solder the other ends of the mono jack wires to the circuit board on the two blobs of solder shown in the red circle.

These are the other side of the pins for the original switch.

CHECK: make sure no solder or wires are connecting the two solder blobs together.

Step 9
Solder the second mono
jack to the circuit board
on the two blobs of solder shown in the red circle, on the right side of the board.

CHECK: make sure no
solder or wires are
connecting the two solder
blobs together.

## MAKER GUIDE


Files available at https://makersmakingchange.com/project/switch-adapted-rc-car-toy/ | Page 6 of 11
Step 10
Solder one of the capacitors to the two solder blobs circled in red in the photo.

These are located just above where the mono jack was
soldered on the left side.
Step 11
With your flush cutters, trim the leads of the capacitor past where they were soldered.
Step 12
Repeat on the right side, solder the capacitor as shown circled in red, and trim the leads.

4

4

## MAKER GUIDE


Files available at https://makersmakingchange.com/project/switch-adapted-rc-car-toy/ | Page 7 of 11
Step 13 – Stop and Test
Put batteries in both the remote and car and test using assistive switches plugged into the mono jacks. When you activate the assistive switch,the LED on the circuit board should light up. If the car is turned on, the assistive switches should imitate the original button functions.
- If LED / car does not turn on when switch is activated, check your connections
- If LED / car stays on when not activating the switch, check your connections
Step 14
Using a permanent marker, mark
where the holes are going to be drilled, above the screw holes and below the battery compartment, as shown circled in the photo.

Make sure these holes aren’t too close to the centre, so they would interfere with the blue piece on the other side. (See photo in next step)

Step 15
Flip the remote around
and check that where
the holes were marked
is not too close to the
rotating blue piece.
This piece is important
for securing the battery
compartment.

If needed, adjust the
location of the drill
holes by making a new
marking. | (In this photo the holes have already been drilled and are far enough
| away to not interfere.)

## MAKER GUIDE


Files available at https://makersmakingchange.com/project/switch-adapted-rc-car-toy/ | Page 8 of 11
Step 16
Using a drill with a ¼ inch drill bit, drill two holes in the remote where you marked them in Step 14.
Step 17
Flip the circuit board around (so the top of the board with the LED is facing up).

Remove the nuts from the
mono jacks and push the input of the mono jacks through the holes you drilled.

## MAKER GUIDE


Files available at https://makersmakingchange.com/project/switch-adapted-rc-car-toy/ | Page 9 of 11
Step 18
Flip around the remote and reinstall the nuts onto the mono jacks. Tighten to secure.

Again, make sure the mono
jacks do not interfere with the blue rotating part.

If the mono jacks do interfere you may need to cut the blue part with your flush cutters so that it can still rotate.

Step 19
Flip the remote around and reinstall the screw that
holds down the circuit
board, shown in yellow.

Make sure no wires are
being pinched.

## MAKER GUIDE


Files available at https://makersmakingchange.com/project/switch-adapted-rc-car-toy/ | Page 10 of 11
Step 20
Take the top half of the remote, facing down, and ensure the red and orange pieces are in the correct spots.

Then carefully take the back half of the remote and place it on top of the front half, lining up all of the screw holes.

Make sure no wires are pinched between the two halves of the remote.

Check that the white antenna wire (circled in red) is going through the proper channels.

Step 21
With the two halves together, replace all of the screws (circled in yellow) and tighten them fully.

Make sure there are batteries in the battery compartment and then rotate the blue piece into place and secure with the screw circled in red.

## MAKER GUIDE


Files available at https://makersmakingchange.com/project/switch-adapted-rc-car-toy/ | Page 11 of 11
Step 22 – Final Test
Plug assistive switches into the mono ports and test the
remote again. Make sure the car is turned on.

Check if both the assistive switch and the original
buttons both work and do the functions intended (forward and reverse).

Note: If the assistive switches worked properly at Step 13, but are now either not turning on or are staying on, you may have a loose connection. Open the remote back up and check.

Step 23
If your switch adapted
remote works as
expected, you are
finished!

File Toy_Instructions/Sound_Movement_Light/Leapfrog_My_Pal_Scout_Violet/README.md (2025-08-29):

# Switch Adapted Leapfrog MyPal Scout and Violet Plush
The MyPal Scout and Violet Plush Toys from Leap Frog have been switch adapted for easy activation using a 3.5 mm switch. 
<!--- PHOTO --->
<p align="center">
 Switch Adapted LeapFrog MyPal Violet Plush Toy
</p>

## More Info at
- [Makers Making Change Project Page] (https://www.makersmakingchange.com/product/switch-adapted-leapfrog-my-pal-scout-plush/01tJR000000690IYAQ)

## Overview
The switch adapted My Pal Scout/Violet sings songs and can be controlled with accessible switches that have a 3.5 mm jack. The My Pal is a LeapFrog toy that sings lullabies and learning songs, and has activities with numbers, animals, food, and more.

## Usage
The MyPal Scout and Violet plush toys have four inputs which can be activated by plugging in four AT switches. 

### Documentation
<!--- DOCUMENTATION --->
| Document | Version | Link |
|----------|---------|------|
| Design Rationale     | 1.0 | []()  |
| Bill of Materials    | 1.0 | []() |
| Maker Guide       | 1.0 | []() |
| User Guide          | 1.0 | []()           |
| Changelog            | 1.0 | []()               |

## License
<!--- LICENSE  Choose an appropriate license. We recommend an open-source hardware compatible license. --->
Everything needed or used to design, make, test, or prepare the Switch Adapted Whale Bubble Blower is licensed under the CERN 2.0 Permissive license <https://ohwr.org/cern_ohl_p_v2.txt> (CERN-OHL-P).

Accompanying material such as instruction manuals, videos, and other copyrightable works that are useful but not necessary to design, make, test, or prepare the Switch Adapted Whale Bubble Blower are published under a Creative Commons Attribution-ShareAlike 4.0 license <https://creativecommons.org/licenses/by-sa/4.0/> (CC BY-SA 4.0).

## Attribution
<!--- ATTRIBUTION Include any information related to the development of the design. This may include who identified the initial challenge, who contributed to the design --->
 - The documentation template was created by Makers Making Change and is used under a CC BY-SA 4.0 license. It is available at the following link: https://github.com/makersmakingchange/OpenAT-Template

<!-- ABOUT MMC START -->
## About Makers Making Change
[Makers Making Change Logo](https://www.makersmakingchange.com/)

Makers Making Change is a program of [Neil Squire](https://www.neilsquire.ca/), a Canadian non-profit that uses technology, knowledge, and passion to empower people with disabilities.

Makers Making Change leverages the capacity of community based Makers, Disability Professionals and Volunteers to develop and deliver affordable Open Source Assistive Technologies.

 - Website: [www.MakersMakingChange.com](https://www.makersmakingchange.com/)
 - GitHub: [makersmakingchange](https://github.com/makersmakingchange)
 - Bluesky: [@makersmakingchange.bsky.social](https://bsky.app/profile/makersmakingchange.bsky.social)
 - Instagram: [@makersmakingchange](https://www.instagram.com/makersmakingchange)
 - Facebook: [makersmakechange](https://www.facebook.com/makersmakechange)
 - LinkedIn: [Neil Squire Society](https://www.linkedin.com/company/neil-squire-society/)
 - Thingiverse: [makersmakingchange](https://www.thingiverse.com/makersmakingchange/about)
 - Printables: [MakersMakingChange](https://www.printables.com/@MakersMakingChange)

### Contact Us
For technical questions, to get involved, or to share your experience we encourage you to [visit our website](https://www.makersmakingchange.com/) or [contact us](https://www.makersmakingchange.com/s/contact).
<!-- ABOUT MMC END -->

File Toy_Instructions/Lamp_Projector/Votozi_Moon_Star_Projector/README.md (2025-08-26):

# Switch Adapted Moon and Star Projector
This folder contains information for how to modify a commercially available Moon and Star Projector for use with an assistive switch.

<!--- PHOTO --->


## More info at
- [Makers Making Change Project Page](https://www.makersmakingchange.com/product/switch-adapted-moon-and-star-projector/01tJR000000694HYAQ)

## Getting Started
<!--- Include an overall idea of what major steps are required to build the device. --->

### 1. Order the Off-The-Shelf Components
The [Bill of Materials](https://github.com/makersmakingchange/Adapted-Toys/blob/e7f703992e87acbce26a720f6fc8d6e3133175c9/Toy_Instructions/Available/Lamp%2BProjector_Toys/Votozi%20-%20Moon%20and%20Star%20Projector/Star_Master_Projector_BOM_V1.0.xlsx) lists all of the parts and components required to build the Switch Adapted Moon and Star Projector. The electronic components may be available locally, but will probably need to be ordered online. 

### 2. Assemble the Moon and Star Projector
Reference the [maker guide](https://github.com/makersmakingchange/Adapted-Toys/blob/f33ee1821fe02120cff16a04218ac82712526dc8/Toy_Instructions/Available/Lamp%2BProjector_Toys/Votozi%20-%20Moon%20and%20Star%20Projector/Star_Master_Projector_Assembly_Guide.pdf) for the tools and steps required to build each portion.

## Files
<!---FILES  This section includes all the information and files required to build and modify the device, including documentation, design files, and build files. --->

### Documentation
<!--- DOCUMENTATION --->
| Document | Version | Link |
|----------|---------|------|
| Bill of Materials    | 1.0 | [MoonStarProjector_BOM](https://github.com/makersmakingchange/Adapted-Toys/blob/e7f703992e87acbce26a720f6fc8d6e3133175c9/Toy_Instructions/Available/Lamp%2BProjector_Toys/Votozi%20-%20Moon%20and%20Star%20Projector/Star_Master_Projector_BOM_V1.0.xlsx) |
| Maker Guide       | 1.0 | [MoonStarProjector_Maker_Guide](https://github.com/makersmakingchange/Adapted-Toys/blob/f33ee1821fe02120cff16a04218ac82712526dc8/Toy_Instructions/Available/Lamp%2BProjector_Toys/Votozi%20-%20Moon%20and%20Star%20Projector/Star_Master_Projector_Assembly_Guide.pdf) |
| User Guide          | 1.0 | [MoonStarProjector_User_Guide](https://github.com/makersmakingchange/Adapted-Toys/blob/5c173dd1146b2fd2b433b0da870c7c3bebae929c/Toy_Instructions/Available/Lamp%2BProjector_Toys/Votozi%20-%20Moon%20and%20Star%20Projector/Star_Master_Projector_User_Guide.pdf)           |
| Maker Checklist            | 1.0 | [MoonStarProjector_Maker_Checklist](https://github.com/makersmakingchange/Adapted-Toys/blob/6f8715865dff660e9b1ca6471f682d3be3c4f8f1/Toy_Instructions/Available/Lamp%2BProjector_Toys/Votozi%20-%20Moon%20and%20Star%20Projector/Star_Master_Projector_Maker_Checklist.pdf)               |
| Summary     | 1.0 | [MoonStarProjector_Summary](https://github.com/makersmakingchange/Adapted-Toys/blob/7f0a7f0399af23effeb7bdf6c89f107aea264be9/Toy_Instructions/Available/Lamp%2BProjector_Toys/Votozi%20-%20Moon%20and%20Star%20Projector/Star_Master_Projector_Summary.pdf)    |

## License
<!---
LICENSE
Choose an appropriate license. We recommend an open-source hardware compatible license.
--->
Everything needed or used to design, make, test, or prepare the Switch Adapted Moon and Star Projector is licensed under the CERN 2.0 Weakly Reciprocal license <https://ohwr.org/cern_ohl_p_v2.txt> (CERN-OHL-W).

Accompanying material such as instruction manuals, videos, and other copyrightable works that are useful but not necessary to design, make, test, or prepare the Switch Adapted Moon and Star Projector are published under a Creative Commons Attribution-ShareAlike 4.0 license <https://creativecommons.org/licenses/by-sa/4.0/> (CC BY-SA 4.0).

## Attribution

The original concept for the toy modification was from the Tinkered Toy Box, a collaboration between Mott Children's Hospital and the Washtenaw Intermediate School District with funding provided by DMUM (Dance Marathon at the University of Michigan).

The documentation template was created by Makers Making Change and is used under a CC BY-SA 4.0 license. It is available at the following link: https://github.com/makersmakingchange/OpenAT-Template

---

<!-- ABOUT MMC START -->
## About Makers Making Change
[Makers Making Change Logo](https://www.makersmakingchange.com/)

Makers Making Change is a program of [Neil Squire](https://www.neilsquire.ca/), a Canadian non-profit that uses technology, knowledge, and passion to empower people with disabilities.

Makers Making Change leverages the capacity of community based Makers, Disability Professionals and Volunteers to develop and deliver affordable Open Source Assistive Technologies.

 - Website: [www.MakersMakingChange.com](https://www.makersmakingchange.com/)
 - GitHub: [makersmakingchange](https://github.com/makersmakingchange)
 - Bluesky: [@makersmakingchange.bsky.social](https://bsky.app/profile/makersmakingchange.bsky.social)
 - Instagram: [@makersmakingchange](https://www.instagram.com/makersmakingchange)
 - Facebook: [makersmakechange](https://www.facebook.com/makersmakechange)
 - LinkedIn: [Neil Squire Society](https://www.linkedin.com/company/neil-squire-society/)
 - Thingiverse: [makersmakingchange](https://www.thingiverse.com/makersmakingchange/about)
 - Printables: [MakersMakingChange](https://www.printables.com/@MakersMakingChange)

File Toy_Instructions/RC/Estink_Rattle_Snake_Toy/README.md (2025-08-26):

# Switch Adapted RC Rattle Snake

## Overview
This repository contains the necessary information to switch adapt a commercially available Remote Control Rattle Snake. 

<!--- PHOTO --->


## Getting Started
<!--- Include an overall idea of what major steps are required to build the device. --->

### 1. Order the Off-The-Shelf Components
The [Bill of Materials](https://github.com/makersmakingchange/Adapted-Toys/blob/61eccf1686d0bf9c07d14af7184d1c0cee148b85/Toy_Instructions/Available/RC_Toys/Estink%20-%20Rattle%20Snake%20Toy/SlitheringSnake_BOM_V1.0.xlsx) lists all of the parts and components required to build the Switch Adapted Whale Bubble Blower. The electronic components may be available locally, but will probably need to be ordered online. 

### 2. Assemble the Switch Adapted Whale Bubble Blower
Reference the [maker guide](https://github.com/makersmakingchange/Adapted-Toys/blob/3ffab351692519d6581d821faf11a66c978a04d9/Toy_Instructions/Available/RC_Toys/Estink%20-%20Rattle%20Snake%20Toy/SlitheringSnake_Assembly_Guide.pdf) for the tools and steps required to build each portion.

## Files
<!---FILES  This section includes all the information and files required to build and modify the device, including documentation, design files, and build files. --->

### Documentation
<!--- DOCUMENTATION --->
| Document | Version | Link |
|----------|---------|------|
| Design Rationale     | 1.0 | [RattleSnake_Design_Rationale](https://github.com/makersmakingchange/Adapted-Toys/blob/5016a3d5ef5db248452a0a430a34345196785bc4/Toy_Instructions/Available/RC_Toys/Estink%20-%20Rattle%20Snake%20Toy/SlitheringSnake_Design_Rationale.pdf) |
| Bill of Materials    | 1.0 | [RattleSnake_BOM](https://github.com/makersmakingchange/Adapted-Toys/blob/61eccf1686d0bf9c07d14af7184d1c0cee148b85/Toy_Instructions/Available/RC_Toys/Estink%20-%20Rattle%20Snake%20Toy/SlitheringSnake_BOM_V1.0.xlsx) |
| Maker Guide       | 1.0 | [RattleSnake_Maker_Guide](https://github.com/makersmakingchange/Adapted-Toys/blob/3ffab351692519d6581d821faf11a66c978a04d9/Toy_Instructions/Available/RC_Toys/Estink%20-%20Rattle%20Snake%20Toy/SlitheringSnake_Assembly_Guide.pdf) |
| User Guide          | 1.0 | [RattleSnake_User_Guide](https://github.com/makersmakingchange/Adapted-Toys/blob/9df766a7123e797589fd489a29e9c6532143bde8/Toy_Instructions/Available/RC_Toys/Estink%20-%20Rattle%20Snake%20Toy/SlitheringSnake_User_Guide.pdf)           |
| Changelog            | 1.0 | [RattleSnake_Changelog](https://github.com/makersmakingchange/Adapted-Toys/blob/5f80e6b7cd08b7e437c9ad23f1a9116060648fcb/Toy_Instructions/Available/RC_Toys/Estink%20-%20Rattle%20Snake%20Toy/SlitheringSnake_ChangeLog.pdf)               |
| 3D Print Guide | 1.0 | [RattleSnake_3D_Print_Guide](https://github.com/makersmakingchange/Adapted-Toys/blob/7300ee1ef6fd14b7e20a9e13d5cae95a1281cb47/Toy_Instructions/Available/RC_Toys/Estink%20-%20Rattle%20Snake%20Toy/SlitheringSnake_3D_Print_Guide.pdf) |
| Maker Checklist | 1.0 | [RattleSnake_Maker_Checklist](https://github.com/makersmakingchange/Adapted-Toys/blob/badd7656d86b0af4fb720fd05f420fd92d215619/Toy_Instructions/Available/RC_Toys/Estink%20-%20Rattle%20Snake%20Toy/SlitheringSnake_Maker_Checklist.pdf) |
| Summary | 1.0 | [RattleSnake_Summary](https://github.com/makersmakingchange/Adapted-Toys/blob/f76a05206dba21f5de912e67a63604873f40087e/Toy_Instructions/Available/RC_Toys/Estink%20-%20Rattle%20Snake%20Toy/SlitheringSnake_Summary.pdf) |
## License
<!--- LICENSE Choose an appropriate license. We recommend an open-source hardware compatible license. --->
Everything needed or used to design, make, test, or prepare the Switch Adapted RC Rattle Snake is licensed under the CERN 2.0 Weakly Reciprocal license <https://ohwr.org/cern_ohl_p_v2.txt> (CERN-OHL-W).

Accompanying material such as instruction manuals, videos, and other copyrightable works that are useful but not necessary to design, make, test, or prepare the Switch Adapted RC Rattle Snake are published under a Creative Commons Attribution-ShareAlike 4.0 license <https://creativecommons.org/licenses/by-sa/4.0/> (CC BY-SA 4.0).

## Attribution
<!--- ATTRIBUTION Include any information related to the development of the design. This may include who identified the initial challenge, who contributed to the design --->

The documentation template was created by Makers Making Change and is used under a CC BY-SA 4.0 license. It is available at the following link: https://github.com/makersmakingchange/OpenAT-Template

----
<!-- ABOUT MMC START -->
## About Makers Making Change
[Makers Making Change Logo](https://www.makersmakingchange.com/)

Makers Making Change is a program of [Neil Squire](https://www.neilsquire.ca/), a Canadian non-profit that uses technology, knowledge, and passion to empower people with disabilities.

Makers Making Change leverages the capacity of community based Makers, Disability Professionals and Volunteers to develop and deliver affordable Open Source Assistive Technologies.

 - Website: [www.MakersMakingChange.com](https://www.makersmakingchange.com/)
 - GitHub: [makersmakingchange](https://github.com/makersmakingchange)
 - Bluesky: [@makersmakingchange.bsky.social](https://bsky.app/profile/makersmakingchange.bsky.social)
 - Instagram: [@makersmakingchange](https://www.instagram.com/makersmakingchange)
 - Facebook: [makersmakechange](https://www.facebook.com/makersmakechange)
 - LinkedIn: [Neil Squire Society](https://www.linkedin.com/company/neil-squire-society/)
 - Thingiverse: [makersmakingchange](https://www.thingiverse.com/makersmakingchange/about)
 - Printables: [MakersMakingChange](https://www.printables.com/@MakersMakingChange)

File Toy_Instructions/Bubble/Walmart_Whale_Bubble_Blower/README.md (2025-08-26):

<!--- Open Source Assistive Technology: GitHub Readme Template --->

 <!--- TITLE Should match the name of the GitHub repository. Choose something descriptive rather than whimsical.  --->
# Switch Adapted Whale Bubble Blower

<!--- SUMMARY A brief summary of the project. What it does, who it is for, how much it costs.  --->
The Switch Adapted Whale Bubble Blower is an adapted “Balnore Bubble Machine” that can be activated with a 3.5mm switch. This adaptation is intended for users who have difficulty activating the button on the side of the bubble machine.

<!--- PHOTO --->


## More info at
 - [Makers Making Change Project Page](https://www.makersmakingchange.com/product/switch-adapted-whale-bubble-blower/01tJR0000008XObYAM)

## Getting Started
<!--- Include an overall idea of what major steps are required to build the device. --->

### 1. Order the Off-The-Shelf Components
The [Bill of Materials](https://github.com/makersmakingchange/Adapted-Toys/blob/a10a22f64e9629dad213601bb911e0a12d49a815/Toy_Instructions/Available/Bubble_Toys/Walmart%20-%20Whale%20Bubble%20Blower/WhaleBubbleBlower_BOM_v1.0.xlsx) lists all of the parts and components required to build the Switch Adapted Whale Bubble Blower. The electronic components may be available locally, but will probably need to be ordered online. 

### 2. Assemble the Switch Adapted Whale Bubble Blower
Reference the [maker guide](https://github.com/makersmakingchange/Adapted-Toys/blob/e83c49276aab2990c4e683baedd8f23d08d3a803/Toy_Instructions/Available/Bubble_Toys/Walmart%20-%20Whale%20Bubble%20Blower/WhaleBubbleBlower_Maker_Guide_v1.0.pdf) for the tools and steps required to build each portion.

## Files
<!---FILES  This section includes all the information and files required to build and modify the device, including documentation, design files, and build files. --->

### Documentation
<!--- DOCUMENTATION --->
| Document | Version | Link |
|----------|---------|------|
| Design Rationale     | 1.0 | [WhaleBubbleBlower_Design_Rationale](https://github.com/makersmakingchange/Adapted-Toys/blob/5c0f1ae4ded83be4f4a40ada07c183d7d166e519/Toy_Instructions/Available/Bubble_Toys/Walmart%20-%20Whale%20Bubble%20Blower/WhaleBubbleBlower_Design_Rationale_v1.0.pdf)  |
| Bill of Materials    | 1.0 | [WhaleBubbleBlower_BOM](https://github.com/makersmakingchange/Adapted-Toys/blob/a10a22f64e9629dad213601bb911e0a12d49a815/Toy_Instructions/Available/Bubble_Toys/Walmart%20-%20Whale%20Bubble%20Blower/WhaleBubbleBlower_BOM_v1.0.xlsx) |
| Maker Guide       | 1.0 | [WhaleBubbleBlower_Maker_Guide](https://github.com/makersmakingchange/Adapted-Toys/blob/e83c49276aab2990c4e683baedd8f23d08d3a803/Toy_Instructions/Available/Bubble_Toys/Walmart%20-%20Whale%20Bubble%20Blower/WhaleBubbleBlower_Maker_Guide_v1.0.pdf) |
| User Guide          | 1.0 | [WhaleBubbleBlower_User_Guide](https://github.com/makersmakingchange/Adapted-Toys/blob/fdeb6ab99f429f457c09a3cf26f13fe69b0b544c/Toy_Instructions/Available/Bubble_Toys/Walmart%20-%20Whale%20Bubble%20Blower/WhaleBubbleBlower_User_Guide_v1.0.pdf)           |
| Changelog            | 1.0 | [WhaleBubbleBlower_Changelog](https://github.com/makersmakingchange/Adapted-Toys/blob/43e2116c8b612cb2f58cdf69b7bc1a573a4398e3/Toy_Instructions/Available/Bubble_Toys/Walmart%20-%20Whale%20Bubble%20Blower/Working%20Documents/WhaleBubbleBlower_Changelog.docx)               |

## License
<!--- LICENSE  Choose an appropriate license. We recommend an open-source hardware compatible license. --->
Everything needed or used to design, make, test, or prepare the Switch Adapted Whale Bubble Blower is licensed under the CERN 2.0 Permissive license <https://ohwr.org/cern_ohl_p_v2.txt> (CERN-OHL-P).

Accompanying material such as instruction manuals, videos, and other copyrightable works that are useful but not necessary to design, make, test, or prepare the Switch Adapted Whale Bubble Blower are published under a Creative Commons Attribution-ShareAlike 4.0 license <https://creativecommons.org/licenses/by-sa/4.0/> (CC BY-SA 4.0).

## Attribution
<!--- ATTRIBUTION Include any information related to the development of the design. This may include who identified the initial challenge, who contributed to the design --->
 - The documentation template was created by Makers Making Change and is used under a CC BY-SA 4.0 license. It is available at the following link: https://github.com/makersmakingchange/OpenAT-Template

<!-- ABOUT MMC START -->
## About Makers Making Change
[Makers Making Change Logo](https://www.makersmakingchange.com/)

Makers Making Change is a program of [Neil Squire](https://www.neilsquire.ca/), a Canadian non-profit that uses technology, knowledge, and passion to empower people with disabilities.

Makers Making Change leverages the capacity of community based Makers, Disability Professionals and Volunteers to develop and deliver affordable Open Source Assistive Technologies.

 - Website: [www.MakersMakingChange.com](https://www.makersmakingchange.com/)
 - GitHub: [makersmakingchange](https://github.com/makersmakingchange)
 - Bluesky: [@makersmakingchange.bsky.social](https://bsky.app/profile/makersmakingchange.bsky.social)
 - Instagram: [@makersmakingchange](https://www.instagram.com/makersmakingchange)
 - Facebook: [makersmakechange](https://www.facebook.com/makersmakechange)
 - LinkedIn: [Neil Squire Society](https://www.linkedin.com/company/neil-squire-society/)
 - Thingiverse: [makersmakingchange](https://www.thingiverse.com/makersmakingchange/about)
 - Printables: [MakersMakingChange](https://www.printables.com/@MakersMakingChange)

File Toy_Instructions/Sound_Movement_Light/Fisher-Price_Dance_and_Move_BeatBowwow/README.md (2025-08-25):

# Switch-Adapted Fisher-Price Beat Bow Wow Toy
If you want an accessingle singing toy dog, the Switch-Adapted Beat Bow Wow from Fisher-Price will get young children dancing and laughing.

These adaptation instructions were developed by, and are attributed to Switched Adapted Toys.

If you're looking for video instructions for a single switch adaptation, click here: https://www.youtube.com/watch?v=45SwBttVEOA

<!-- ABOUT MMC START -->
## About Makers Making Change
[Makers Making Change Logo](https://www.makersmakingchange.com/)

Makers Making Change is a program of [Neil Squire](https://www.neilsquire.ca/), a Canadian non-profit that uses technology, knowledge, and passion to empower people with disabilities.

Makers Making Change leverages the capacity of community based Makers, Disability Professionals and Volunteers to develop and deliver affordable Open Source Assistive Technologies.

 - Website: [www.MakersMakingChange.com](https://www.makersmakingchange.com/)
 - GitHub: [makersmakingchange](https://github.com/makersmakingchange)
 - Bluesky: [@makersmakingchange.bsky.social](https://bsky.app/profile/makersmakingchange.bsky.social)
 - Instagram: [@makersmakingchange](https://www.instagram.com/makersmakingchange)
 - Facebook: [makersmakechange](https://www.facebook.com/makersmakechange)
 - LinkedIn: [Neil Squire Society](https://www.linkedin.com/company/neil-squire-society/)
 - Thingiverse: [makersmakingchange](https://www.thingiverse.com/makersmakingchange/about)
 - Printables: [MakersMakingChange](https://www.printables.com/@MakersMakingChange)

### Contact Us
For technical questions, to get involved, or to share your experience we encourage you to [visit our website](https://www.makersmakingchange.com/) or [contact us](https://www.makersmakingchange.com/s/contact).
<!-- ABOUT MMC END -->

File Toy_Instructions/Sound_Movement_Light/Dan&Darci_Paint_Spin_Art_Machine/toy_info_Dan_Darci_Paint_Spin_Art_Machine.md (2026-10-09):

---
# Fill in the value after each colon, on the SAME line as the field -
# don't press Enter partway through a value. Leave a field completely
# blank (nothing after the colon) if you don't have that info yet.
last_updated: 2026-10-09              # yyyy-mm-dd - date this file was last updated
toy_features:                # keep only the relevant lines below, delete the rest
  - Movement
  - Art
activation_type:            # keep only the relevant lines below, delete the rest
  - Press and Hold
requires_3d_printing: No    # Yes or No
adaptation_method:          # keep only the relevant lines below, delete the rest
  - Mono Jack + Wire
number_of_switches:         # keep only the relevant lines below, delete the rest
  - 1
hfth_collection_year: 2026       # e.g. 2026 - leave blank if never part of a HFTH collection
available_to_purchase: Yes  # Yes or No - is the toy still available to purchase?
toy_purchase_link: https://www.amazon.ca/dp/B0CJYKM4FT         # adds a "Where to Buy This Toy" button if filled in
toy_purchase_link_alt:     # adds a 2nd purchase button if there's another link
general_notes:               # any general notes, e.g. "Uses lots of screws."
device_uid:                  # internal MMC use only - never shown on the site
name:                        # only fill in to OVERRIDE the auto name - else leave blank
category:                    # only fill in to OVERRIDE the auto category - else leave blank
link:                        # only fill in to OVERRIDE the auto GitHub link - else leave blank
battery_type: AA
battery_required: 4
battery_included:            # number of batteries included
contributers:              # names of contributers to the instructions / this design
---

Every child deserves to play. But for many kids with disabilities, toys can be hard to use independently, and commercially adapted versions can run upwards of $300. However, with a little bit of tinkering, we can switch-adapt toys and make them accessible for a fraction of the cost.

Annually, from September to December Makers Making Change hosts the [Hacking for the Holidays](https://www.makersmakingchange.com/hacking-for-the-holidays) campaign, where we engage volunteers — students, corporate partners, and other community members — in many build events across Canada to help us adapt and donate thousands of toys and switches to families and clinicians all over Canada.

Please note the information on this page is only accurate to when it was last updated.

If you are looking for more information on where to purchase the materials to adapt a toy, please visit the [Common Component and Tool page](https://makersmakingchange.github.io/Switch_Adapted_Toys/toy-components-and-tools/) on this resource.

<!--
  Everything above this line (outside the --- --- block at the top) is
  just for humans reading this file - it isn't read by the site build.
  This same text already shows automatically on every toy's page, so you
  don't need to copy/edit it per toy; it's here for context only.

  ONE IMPORTANT RULE for the fields inside the --- --- block above:
  keep every value on the SAME line as its field name. If a value
  wraps onto a second line by accident (e.g. a long name spilling onto
  a new line without quotes), that whole wrapped block gets silently
  read as one long piece of text - which can also swallow the field(s)
  that come right after it. If you ever need to double check a field
  looks right, open this file on GitHub and confirm nothing after a
  colon spills onto its own new line unless it's a "- " list item.
-->

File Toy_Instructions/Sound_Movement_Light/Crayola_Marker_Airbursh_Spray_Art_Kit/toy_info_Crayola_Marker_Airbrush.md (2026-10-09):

---
# Fill in the value after each colon, on the SAME line as the field -
# don't press Enter partway through a value. Leave a field completely
# blank (nothing after the colon) if you don't have that info yet.
last_updated:               # yyyy-mm-dd - date this file was last updated
toy_features:                # keep only the relevant lines below, delete the rest
  - Movement
  - Art
activation_type:            # keep only the relevant lines below, delete the rest
  - Press and Hold
requires_3d_printing: No    # Yes or No
adaptation_method:          # keep only the relevant lines below, delete the rest
  - Mono Jack + Wire
number_of_switches:         # keep only the relevant lines below, delete the rest
  - 1
hfth_collection_year: 2026       # e.g. 2026 - leave blank if never part of a HFTH collection
available_to_purchase: Yes  # Yes or No - is the toy still available to purchase?
toy_purchase_link: https://www.walmart.ca/en/ip/Crayola-Marker-Airbrush-Art-Kit/1HPWVN49J48X         # adds a "Where to Buy This Toy" button if filled in
toy_purchase_link_alt: https://www.amazon.ca/Crayola-45205-Marker-Airbrush/dp/B0F6T2XWJL/ref=asc_df_B0F6T2XWJL     # adds a 2nd purchase button if there's another link
general_notes: Requires a triangle screwdriver              # any general notes, e.g. "Uses lots of screws."
device_uid:                  # internal MMC use only - never shown on the site
name:                        # only fill in to OVERRIDE the auto name - else leave blank
category:                    # only fill in to OVERRIDE the auto category - else leave blank
link:                        # only fill in to OVERRIDE the auto GitHub link - else leave blank
battery_type: AA
battery_required: 4
battery_included:            # number of batteries included
contributers: Shanelle Gilman             # names of contributers to the instructions / this design
---

Every child deserves to play. But for many kids with disabilities, toys can be hard to use independently, and commercially adapted versions can run upwards of $300. However, with a little bit of tinkering, we can switch-adapt toys and make them accessible for a fraction of the cost.

Annually, from September to December Makers Making Change hosts the [Hacking for the Holidays](https://www.makersmakingchange.com/hacking-for-the-holidays) campaign, where we engage volunteers — students, corporate partners, and other community members — in many build events across Canada to help us adapt and donate thousands of toys and switches to families and clinicians all over Canada.

Please note the information on this page is only accurate to when it was last updated.

If you are looking for more information on where to purchase the materials to adapt a toy, please visit the [Common Component and Tool page](https://makersmakingchange.github.io/Switch_Adapted_Toys/toy-components-and-tools/) on this resource.

<!--
  Everything above this line (outside the --- --- block at the top) is
  just for humans reading this file - it isn't read by the site build.
  This same text already shows automatically on every toy's page, so you
  don't need to copy/edit it per toy; it's here for context only.

  ONE IMPORTANT RULE for the fields inside the --- --- block above:
  keep every value on the SAME line as its field name. If a value
  wraps onto a second line by accident (e.g. a long name spilling onto
  a new line without quotes), that whole wrapped block gets silently
  read as one long piece of text - which can also swallow the field(s)
  that come right after it. If you ever need to double check a field
  looks right, open this file on GitHub and confirm nothing after a
  colon spills onto its own new line unless it's a "- " list item.
-->

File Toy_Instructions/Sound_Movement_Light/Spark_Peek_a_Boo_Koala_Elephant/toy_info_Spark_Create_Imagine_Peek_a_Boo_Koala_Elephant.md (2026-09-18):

---
# Fill in the value after each colon, on the SAME line as the field -
# don't press Enter partway through a value. Leave a field completely
# blank (nothing after the colon) if you don't have that info yet.
last_updated: 2026-08-21               # yyyy-mm-dd - date this file was last updated
toy_features:                # keep only the relevant lines below, delete the rest
  - Movement
  - Sound
activation_type:            # keep only the relevant lines below, delete the rest
  - Single Press
requires_3d_printing: No    # Yes or No
adaptation_method:          # keep only the relevant lines below, delete the rest
  - Mono Cable
number_of_switches:         # keep only the relevant lines below, delete the rest
  - 2
hfth_collection_year:       # e.g. 2026 - leave blank if never part of a HFTH collection
available_to_purchase: Yes  # Yes or No - is the toy still available to purchase?
toy_purchase_link: https://www.walmart.ca/en/ip/Spark-Create-Imagine-Peek-a-Boo-Koala/6000208880006?classType=REGULAR&from=/search          # adds a "Where to Buy This Toy" button if filled in
toy_purchase_link_alt: https://www.walmart.ca/en/ip/Spark-Create-Imagine-Peek-A-Boo-Elephant/6000207307778?classType=REGULAR&from=/search     # adds a 2nd purchase button if there's another link
general_notes: Moderate -Board hard to solder to               # any general notes, e.g. "Uses lots of screws."
device_uid:                  # internal MMC use only - never shown on the site
name:                        # only fill in to OVERRIDE the auto name - else leave blank
category:                    # only fill in to OVERRIDE the auto category - else leave blank
link:                        # only fill in to OVERRIDE the auto GitHub link - else leave blank
battery_type: AA
battery_required: 3
battery_included:
---

Every child deserves to play. But for many kids with disabilities, toys can be hard to use independently, and commercially adapted versions can run upwards of $300. However, with a little bit of tinkering, we can switch-adapt toys and make them accessible for a fraction of the cost.

Annually, from September to December Makers Making Change hosts the [Hacking for the Holidays](https://www.makersmakingchange.com/hacking-for-the-holidays) campaign, where we engage volunteers — students, corporate partners, and other community members — in many build events across Canada to help us adapt and donate thousands of toys and switches to families and clinicians all over Canada.

Please note the information on this page is only accurate to when it was last updated.

If you are looking for more information on where to purchase the materials to adapt a toy, please visit the [Common Component and Tool page](https://makersmakingchange.github.io/Switch_Adapted_Toys/toy-components-and-tools/) on this resource.

<!--
  Everything above this line (outside the --- --- block at the top) is
  just for humans reading this file - it isn't read by the site build.
  This same text already shows automatically on every toy's page, so you
  don't need to copy/edit it per toy; it's here for context only.

  ONE IMPORTANT RULE for the fields inside the --- --- block above:
  keep every value on the SAME line as its field name. If a value
  wraps onto a second line by accident (e.g. a long name spilling onto
  a new line without quotes), that whole wrapped block gets silently
  read as one long piece of text - which can also swallow the field(s)
  that come right after it. If you ever need to double check a field
  looks right, open this file on GitHub and confirm nothing after a
  colon spills onto its own new line unless it's a "- " list item.
-->

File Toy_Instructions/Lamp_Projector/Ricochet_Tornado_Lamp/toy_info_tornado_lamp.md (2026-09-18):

---
# Fill in the value after each colon, on the SAME line as the field -
# don't press Enter partway through a value. Leave a field completely
# blank (nothing after the colon) if you don't have that info yet.
last_updated: 2026-09-18               # yyyy-mm-dd - date this file was last updated
toy_features:                # keep only the relevant lines below, delete the rest
  - Light
activation_type:            # keep only the relevant lines below, delete the rest
  - Press and Hold
requires_3d_printing: No    # Yes or No
adaptation_method:          # keep only the relevant lines below, delete the rest
  - Mono Cable
number_of_switches:         # keep only the relevant lines below, delete the rest
  - 1
hfth_collection_year: 2026      # e.g. 2026 - leave blank if never part of a HFTH collection
available_to_purchase: Yes  # Yes or No - is the toy still available to purchase?
toy_purchase_link:           # adds a "Where to Buy This Toy" button if filled in
toy_purchase_link_alt:      # adds a 2nd purchase button if there's another link
general_notes: beginner, purchase in store at Canadian Tire               # any general notes, e.g. "Uses lots of screws."
device_uid:                  # internal MMC use only - never shown on the site
name:                        # only fill in to OVERRIDE the auto name - else leave blank
category:                    # only fill in to OVERRIDE the auto category - else leave blank
link:                        # only fill in to OVERRIDE the auto GitHub link - else leave blank
battery_type: 
battery_required: 
battery_included:
---

Every child deserves to play. But for many kids with disabilities, toys can be hard to use independently, and commercially adapted versions can run upwards of $300. However, with a little bit of tinkering, we can switch-adapt toys and make them accessible for a fraction of the cost.

Annually, from September to December Makers Making Change hosts the [Hacking for the Holidays](https://www.makersmakingchange.com/hacking-for-the-holidays) campaign, where we engage volunteers — students, corporate partners, and other community members — in many build events across Canada to help us adapt and donate thousands of toys and switches to families and clinicians all over Canada.

Please note the information on this page is only accurate to when it was last updated.

If you are looking for more information on where to purchase the materials to adapt a toy, please visit the [Common Component and Tool page](https://makersmakingchange.github.io/Switch_Adapted_Toys/toy-components-and-tools/) on this resource.

<!--
  Everything above this line (outside the --- --- block at the top) is
  just for humans reading this file - it isn't read by the site build.
  This same text already shows automatically on every toy's page, so you
  don't need to copy/edit it per toy; it's here for context only.

  ONE IMPORTANT RULE for the fields inside the --- --- block above:
  keep every value on the SAME line as its field name. If a value
  wraps onto a second line by accident (e.g. a long name spilling onto
  a new line without quotes), that whole wrapped block gets silently
  read as one long piece of text - which can also swallow the field(s)
  that come right after it. If you ever need to double check a field
  looks right, open this file on GitHub and confirm nothing after a
  colon spills onto its own new line unless it's a "- " list item.
-->

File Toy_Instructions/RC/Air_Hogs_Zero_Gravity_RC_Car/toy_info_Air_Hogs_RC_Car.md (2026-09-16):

---
# Fill in the value after each colon, on the SAME line as the field -
# don't press Enter partway through a value. Leave a field completely
# blank (nothing after the colon) if you don't have that info yet.
last_updated: 2026-08-21               # yyyy-mm-dd - date this file was last updated
toy_features:                # keep only the relevant lines below, delete the rest
  - RC
activation_type:            # keep only the relevant lines below, delete the rest
  - Press and Hold
requires_3d_printing: Yes    # Yes or No
adaptation_method:          # keep only the relevant lines below, delete the rest
  - Mono Cable
number_of_switches:         # keep only the relevant lines below, delete the rest
  - 4
hfth_collection_year: 2026       # e.g. 2026 - leave blank if never part of a HFTH collection
available_to_purchase: Yes  # Yes or No - is the toy still available to purchase?
toy_purchase_link: https://www.amazon.ca/dp/B0BRT9C5S2          # adds a "Where to Buy This Toy" button if filled in
toy_purchase_link_alt:      # adds a 2nd purchase button if there's another link
general_notes: Moderate- multiple solder points               # any general notes, e.g. "Uses lots of screws."
device_uid:                  # internal MMC use only - never shown on the site
name:                        # only fill in to OVERRIDE the auto name - else leave blank
category:                    # only fill in to OVERRIDE the auto category - else leave blank
link:                        # only fill in to OVERRIDE the auto GitHub link - else leave blank
battery_type: AAA
battery_required: 2
battery_included:
---

Every child deserves to play. But for many kids with disabilities, toys can be hard to use independently, and commercially adapted versions can run upwards of $300. However, with a little bit of tinkering, we can switch-adapt toys and make them accessible for a fraction of the cost.

Annually, from September to December Makers Making Change hosts the [Hacking for the Holidays](https://www.makersmakingchange.com/hacking-for-the-holidays) campaign, where we engage volunteers — students, corporate partners, and other community members — in many build events across Canada to help us adapt and donate thousands of toys and switches to families and clinicians all over Canada.

Please note the information on this page is only accurate to when it was last updated.

If you are looking for more information on where to purchase the materials to adapt a toy, please visit the [Common Component and Tool page](https://makersmakingchange.github.io/Switch_Adapted_Toys/toy-components-and-tools/) on this resource.

<!--
  Everything above this line (outside the --- --- block at the top) is
  just for humans reading this file - it isn't read by the site build.
  This same text already shows automatically on every toy's page, so you
  don't need to copy/edit it per toy; it's here for context only.

  ONE IMPORTANT RULE for the fields inside the --- --- block above:
  keep every value on the SAME line as its field name. If a value
  wraps onto a second line by accident (e.g. a long name spilling onto
  a new line without quotes), that whole wrapped block gets silently
  read as one long piece of text - which can also swallow the field(s)
  that come right after it. If you ever need to double check a field
  looks right, open this file on GitHub and confirm nothing after a
  colon spills onto its own new line unless it's a "- " list item.
-->

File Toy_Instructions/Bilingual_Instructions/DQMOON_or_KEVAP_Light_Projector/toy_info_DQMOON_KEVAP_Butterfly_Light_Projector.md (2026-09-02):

---
# Fill in the value after each colon, on the SAME line as the field -
# don't press Enter partway through a value. Leave a field completely
# blank (nothing after the colon) if you don't have that info yet.
last_updated: 2026-08-21               # yyyy-mm-dd - date this file was last updated
toy_features:                # keep only the relevant lines below, delete the rest
  - Light
  - Lamp/Projector
  - French instructions
activation_type:            # keep only the relevant lines below, delete the rest
  - Press and Hold
requires_3d_printing: No    # Yes or No
adaptation_method:          # keep only the relevant lines below, delete the rest
  - Mono Cable
number_of_switches:         # keep only the relevant lines below, delete the rest
  - 3
hfth_collection_year:       # e.g. 2026 - leave blank if never part of a HFTH collection
available_to_purchase: No  # Yes or No - is the toy still available to purchase?
toy_purchase_link: https://a.co/d/dL4bDjU          # adds a "Where to Buy This Toy" button if filled in
toy_purchase_link_alt:      # adds a 2nd purchase button if there's another link
general_notes: moderate multiple solder points, instructions in English and French               # any general notes, e.g. "Uses lots of screws."
device_uid:                  # internal MMC use only - never shown on the site
name:                        # only fill in to OVERRIDE the auto name - else leave blank
category:                    # only fill in to OVERRIDE the auto category - else leave blank
link:                        # only fill in to OVERRIDE the auto GitHub link - else leave blank
battery_type: 
battery_required: 
battery_included:
---

Every child deserves to play. But for many kids with disabilities, toys can be hard to use independently, and commercially adapted versions can run upwards of $300. However, with a little bit of tinkering, we can switch-adapt toys and make them accessible for a fraction of the cost.

Annually, from September to December Makers Making Change hosts the [Hacking for the Holidays](https://www.makersmakingchange.com/hacking-for-the-holidays) campaign, where we engage volunteers — students, corporate partners, and other community members — in many build events across Canada to help us adapt and donate thousands of toys and switches to families and clinicians all over Canada.

Please note the information on this page is only accurate to when it was last updated.

If you are looking for more information on where to purchase the materials to adapt a toy, please visit the [Common Component and Tool page](https://makersmakingchange.github.io/Switch_Adapted_Toys/toy-components-and-tools/) on this resource.

<!--
  Everything above this line (outside the --- --- block at the top) is
  just for humans reading this file - it isn't read by the site build.
  This same text already shows automatically on every toy's page, so you
  don't need to copy/edit it per toy; it's here for context only.

  ONE IMPORTANT RULE for the fields inside the --- --- block above:
  keep every value on the SAME line as its field name. If a value
  wraps onto a second line by accident (e.g. a long name spilling onto
  a new line without quotes), that whole wrapped block gets silently
  read as one long piece of text - which can also swallow the field(s)
  that come right after it. If you ever need to double check a field
  looks right, open this file on GitHub and confirm nothing after a
  colon spills onto its own new line unless it's a "- " list item.
-->

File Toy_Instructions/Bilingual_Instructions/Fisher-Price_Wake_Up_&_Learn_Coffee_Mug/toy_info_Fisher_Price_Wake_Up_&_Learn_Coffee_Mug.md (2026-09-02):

---
# Fill in the value after each colon, on the SAME line as the field -
# don't press Enter partway through a value. Leave a field completely
# blank (nothing after the colon) if you don't have that info yet.
last_updated: 2026-08-21               # yyyy-mm-dd - date this file was last updated
toy_features:                # keep only the relevant lines below, delete the rest
  - Sound
  - Light
  - French instructions
activation_type:            # keep only the relevant lines below, delete the rest
  - Single Press
requires_3d_printing: No    # Yes or No
adaptation_method:          # keep only the relevant lines below, delete the rest
  - Mono Jack + Wire
number_of_switches:         # keep only the relevant lines below, delete the rest
  - 2
hfth_collection_year: 2026       # e.g. 2026 - leave blank if never part of a HFTH collection
available_to_purchase: Yes  # Yes or No - is the toy still available to purchase?
toy_purchase_link: https://www.walmart.ca/en/ip/Fisher-Price-Laugh-Learn-Wake-Up-Learn-Coffee-Mug-Baby-Toddler-Toy-with-Music-Lights-Brown-Green/6000208718549    # adds a "Where to Buy This Toy" button if filled in
toy_purchase_link_alt: https://www.amazon.ca/Fisher-Price-Toddler-Coffee-Learning-Content/dp/B0CBQV2FBV/      # adds a 2nd purchase button if there's another link
general_notes: Moderate difficulty, instructions in English and French              # any general notes, e.g. "Uses lots of screws."
device_uid:                  # internal MMC use only - never shown on the site
name:                        # only fill in to OVERRIDE the auto name - else leave blank
category:                    # only fill in to OVERRIDE the auto category - else leave blank
link:                        # only fill in to OVERRIDE the auto GitHub link - else leave blank
battery_type: LR 44
battery_required: 3
battery_included:
---

Every child deserves to play. But for many kids with disabilities, toys can be hard to use independently, and commercially adapted versions can run upwards of $300. However, with a little bit of tinkering, we can switch-adapt toys and make them accessible for a fraction of the cost.

Annually, from September to December Makers Making Change hosts the [Hacking for the Holidays](https://www.makersmakingchange.com/hacking-for-the-holidays) campaign, where we engage volunteers — students, corporate partners, and other community members — in many build events across Canada to help us adapt and donate thousands of toys and switches to families and clinicians all over Canada.

Please note the information on this page is only accurate to when it was last updated.

If you are looking for more information on where to purchase the materials to adapt a toy, please visit the [Common Component and Tool page](https://makersmakingchange.github.io/Switch_Adapted_Toys/toy-components-and-tools/) on this resource.

<!--
  Everything above this line (outside the --- --- block at the top) is
  just for humans reading this file - it isn't read by the site build.
  This same text already shows automatically on every toy's page, so you
  don't need to copy/edit it per toy; it's here for context only.

  ONE IMPORTANT RULE for the fields inside the --- --- block above:
  keep every value on the SAME line as its field name. If a value
  wraps onto a second line by accident (e.g. a long name spilling onto
  a new line without quotes), that whole wrapped block gets silently
  read as one long piece of text - which can also swallow the field(s)
  that come right after it. If you ever need to double check a field
  looks right, open this file on GitHub and confirm nothing after a
  colon spills onto its own new line unless it's a "- " list item.
-->

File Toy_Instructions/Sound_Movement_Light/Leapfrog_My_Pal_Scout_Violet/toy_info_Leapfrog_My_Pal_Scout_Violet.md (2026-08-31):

---
# Fill in the value after each colon, on the SAME line as the field -
# don't press Enter partway through a value. Leave a field completely
# blank (nothing after the colon) if you don't have that info yet.
last_updated: 2026-08-31               # yyyy-mm-dd - date this file was last updated
toy_features:                # keep only the relevant lines below, delete the rest
  - Sound
activation_type:            # keep only the relevant lines below, delete the rest
  - Single Press
requires_3d_printing: Yes    # Yes or No
adaptation_method:          # keep only the relevant lines below, delete the rest
  - Mono Cable
number_of_switches:         # keep only the relevant lines below, delete the rest
  - 4
hfth_collection_year: 2026       # e.g. 2026 - leave blank if never part of a HFTH collection
available_to_purchase: Yes  # Yes or No - is the toy still available to purchase?
toy_purchase_link: https://www.walmart.ca/en/ip/LeapFrog-My-Pal-Violet-Smarty-Paws-Personalized-Plush-Puppy-English-Version/7CU457U03CMA          # adds a "Where to Buy This Toy" button if filled in
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

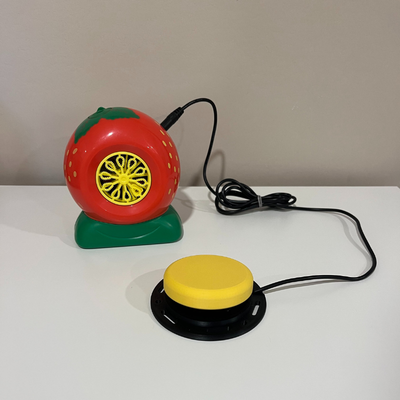
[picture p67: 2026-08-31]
Toy_Instructions/Bubble/Playday_Strawberry_Bubble_Blower/Switch Adapted Play Day Strawberry Bubble Blower.png

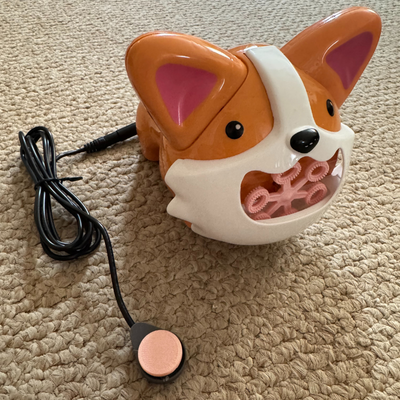
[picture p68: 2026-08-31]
Toy_Instructions/Bubble/Danaplay_Corgi_Bubble_Blower/Switch Adapted Danaplay Corgi Bubble Blower.png

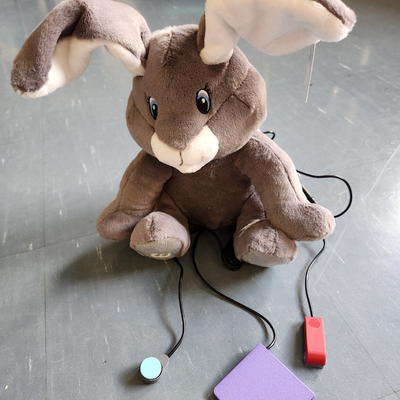
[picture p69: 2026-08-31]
Toy_Instructions/Sound_Movement_Light/Dimple_Peek_a_Boo_Elephant_Bunny/Dimple Peek A Boo Bunny.png

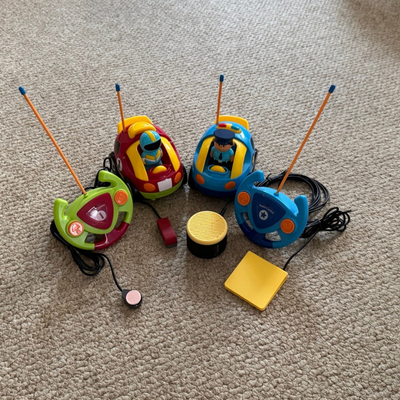
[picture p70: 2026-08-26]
Toy_Instructions/RC/Pretex_Elovien_RC_Race_and_Police_Car/0_Switch_Adapted_RC_Police_and_Race_Car.png

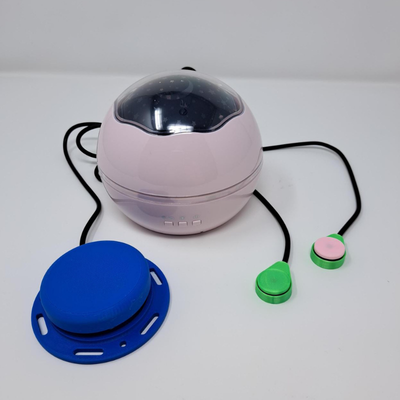
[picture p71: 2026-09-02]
Toy_Instructions/Bilingual_Instructions/DQMOON_or_KEVAP_Light_Projector/Switch Adapted KEVAP Light Projector Off.png

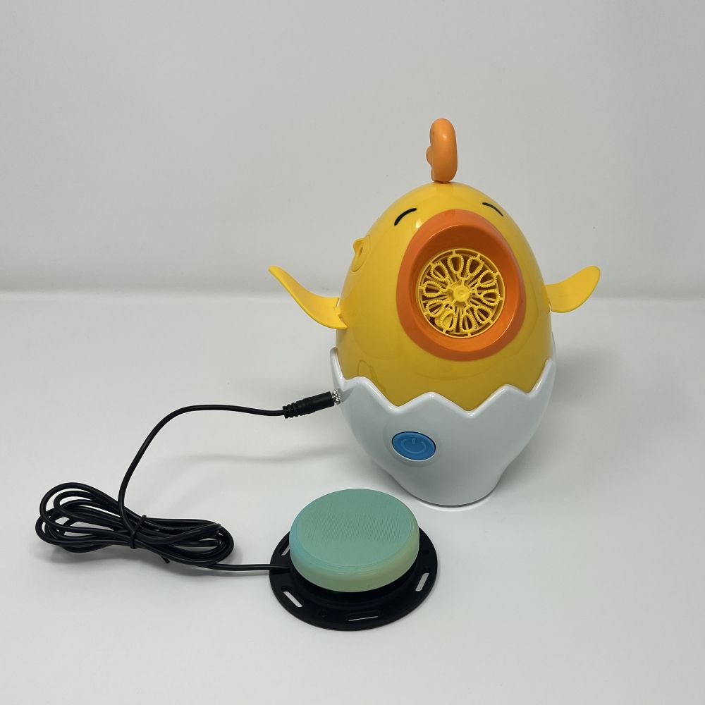
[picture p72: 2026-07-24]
Toy_Instructions/Bubble/Playday_Dancing_Chick_Bubble_Blower/Dancing_Chick_Bubble_Blower.jpg

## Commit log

2025-07-29 Rename Bluey - No-Spill Musical Bubble Machine - Assembly Guide.pdf to Bluey_No-SpillMusicalBubbleMachine_AssemblyGuide_V1.0
2025-07-29 Rename Toy_Instructions/Available_Toys/Bubble_Toys/Bluey - No-Spill Musical Bubble Machine - Assembly Guide.docx to Toy_Instructions/Available_Toys/Bubble_Toys/Working Documents/Bluey - No-Spill Musi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
2025-07-29 Create 3D Printing Files
2025-07-30 Rename Sunny Days - Barney Bubble Baton Assembly Guide v1.0 .pdf to Sunny Days - Barney Bubble Baton - Assembly Guide v1.0 .pdf
2025-07-30 Rename DanaPlay - Corgi Bubble Blower - Assembly Guide V1.0.pdf to DanaPlay - Corgi Bubble Blower - Assembly Guide v1.0.pdf
2025-07-30 Rename DOLLAR~1.PDF to Dollarama - Motorized Bubble Machine - Assembly Guide_V1.0
2025-08-07 Rename Playskool - Stack 'n Spin Monkey Gears Assembly Guide v1.1.docx to Playskool - Stack 'n Spin Monkey Gears - Assembly Guide v1.1.docx
2025-08-14 Rename Wand_Cover_v0.3.1.stl to DELETE Wand_Cover_v0.3.1.stl
    [DELETE Wand_Cover_v0.3.1.stl]
2025-08-14 Rename Wand_Base_v0.3.stl to DELETE Wand_Base_v0.3.stl
    [DELETE Wand_Base_v0.3.stl]
2025-08-25 Rename Kid Connection - Spinning Light Wand - Battery Interupter Assembly Guide V1.1.pdf to Kid Connection - SLW- Battery Interrupter Assembly Guide V1.1.pdf
2025-08-25 Rename Kid Connection - SLW- Battery Interrupter Assembly Guide V1.1.pdf to KC-SLW-BI Assembly Guide V1.1.pdf
2025-08-25 Rename Kid Connection-SLW-BI Assembly Guide V1.1.pdf to V.1.1
2025-08-25 Rename Kid Connection - Spinning Light Wand - Battery Interupter Assembly Guide V1.1.docx to V1.1
2025-08-25 Changed Folder Names for Available and Unavailable Toys
    [Base.stl, Base_Bottom_Cover.stl, Bolt_Stand.stl, Boppin'Beaver_BOM_V1.0.xlsx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]
2025-08-25 Created Folder for each Bubble Toy, and Moved Working Docs into Each Folder
    [Switch_Adapted_Bubble_Blower_BOM.xlsx, WhaleBubbleBlower_BOM.xlsx]
2025-08-26 Changed bubble blaster folder name
    [Cable_Tie_Holder_Back.stl, Cable_Tie_Holder_Front.stl]
2025-08-26 Changed tornado bubble machine file name
    [Switch_Adapted_Bubble_Blower_BOM.xlsx]
2025-08-26 Moved peppa pigs working docs
    [Peppa_Pig_BOM.xlsx]
2025-08-26 Moved working documents into toy folders for all available sound, movement and light up toys
    [Spinning_Light_Wand_BOM_V1.1.xlsx]
2025-08-26 Organized nerf hyperfire files
    [Switch_Adapted_Nerf_Gun_BOM.xlsx, Switch_Adapted_Nerf_Gun_BOM_V1.0.xlsx]
2025-08-26 Organized unavailable bubble toy folders
    [BubbleBlowerFan_BOM.xlsx]
2025-08-26 Organized unavailable sound, movement and light up folders
    [Boppin'Beaver_BOM_V1.0.xlsx, Penguin_Switch_Adapted_Toy_BOM.xlsx, Spin_Art_BOM_V1.0.xlsx]
2025-08-26 Rename Nerf - N-Strike Elite HyperFire Blaster - Assembly Guide V1.0.pdf to Switch_Adapted_Nerf_Gun_Assembly_Guide_V1.0
2025-08-26 Rename Nerf - N-Strike Elite HyperFire Blaster - Assembly Guide V2.0.docx to Switch_Adapted_Nerf_Gun_Assembly_Guide_V1.0
2025-08-26 Delete Build_Files directory
    Remove unneeded template elements
    [OpenAT_Placard.stl]
2025-08-26 Delete Design_Files directory
    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
    [OpenAT_Placard.f3d]
2025-08-26 Delete Documentation directory
    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
    [Device_Name_BOM.csv, Device_Name_BOM.xlsx]
2025-08-27 Rename Dollarama - Motorized Bubble Machine - Assembly Guide_v1.0.docx to Dollarama - Motorized Bubble Machine - Assembly Guide V1.0.docx
2025-08-27 Rename Dollarama - Motorized Bubble Machine - Assembly Guide_v1.0.pdf to Dollarama - Motorized Bubble Machine - Assembly Guide V1.0.pdf
2025-08-27 Rename Fubbles - Light-Up Mini Bubble Machine - Assembly Guide.docx to Fubbles - Light-Up Mini Bubble Machine - Assembly Guide V1.0.docx
2025-08-27 Rename Fubbles - Light-Up Mini Bubble Machine - Assembly Guide.pdf to Fubbles - Light-Up Mini Bubble Machine - Assembly Guide V1.0.pdf
2025-08-27 Rename Gazillion - Hurricane Bubble Machine - Assembly Guide.docx to Gazillion - Hurricane Bubble Machine - Assembly Guide V1.0.docx
2025-08-27 Rename Gazillion - Hurricane Bubble Machine - Assembly Guide.pdf to Gazillion - Hurricane Bubble Machine - Assembly Guide V1.0.pdf
2025-08-27 Rename Gazillion - Tornado Bubble Machine - Assembly Guide.pdf to Gazillion - Tornado Bubble Machine - Assembly Guide V1.0.pdf
2025-08-27 Rename Gazillion - Tornado Bubble Machine - Assembly Guide.docx to Gazillion - Tornado Bubble Machine - Assembly Guide V1.0.docx
2025-08-27 Create Mono Cable Assembly Guide
2025-08-27 Rename Amazon - Dinosour RC Car - Assembly Guide V2.0.docx to Amazon - Dinosour RC Car - Assembly Guide V1.0.docx
2025-08-27 Rename Amazon - Dinosour RC Car - Assembly Guide V2.0.pdf to Amazon - Dinosour RC Car - Assembly Guide V1.0.pdf
2025-08-27 Rename Pretex - RC Truck and Tractor - Assembly Guide V2.0.pdf to Pretex - RC Truck and Tractor - Assembly Guide V1.0.pdf
2025-08-27 Rename Baby Einstein - Glow & Discover Light Bar - Assembly Guide.docx to Baby Einstein - Glow & Discover Light Bar - Assembly Guide V1.0.docx
2025-08-27 Rename Baby Einstein - Glow & Discover Light Bar - Assembly Guide.pdf to Baby Einstein - Glow & Discover Light Bar - Assembly Guide V1.0.pdf
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2025-08-27 Renamed print files to 3D print files
    [monojackboxbase.stl, monojackboxlid.stl]
2025-08-29 Renamed Toy Categories
    [Base.stl, Base_Bottom_Cover.stl, Bolt_Stand.stl, Boppin'Beaver_BOM_V1.0.xlsx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]
2025-08-29 Updated the bubble blower folder names
    [Cable_Tie_Holder_Back.stl, Cable_Tie_Holder_Front.stl, Switch_Adapted_Bubble_Blower_BOM.xlsx, WhaleBubbleBlower_BOM.xlsx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]
2025-08-29 Renamed all available bubble file names
    [Cable_Tie_Holder_Back.stl, Cable_Tie_Holder_Front.stl, Gazillion_Tornado_Bubble_Machine_BOM.xlsx, Walmart_Whale_Bubble_Blower_BOM.xlsx]
2025-08-29 Renamed lamp and projector file names
    [Votozi_Moon_Star_Projector_BOM.xlsx]
2025-08-29 Renamed all available RC file names
    [Estink_Rattle_Snake_Toy_BOM.xlsx, monojackboxbase.stl, monojackboxlid.stl]
2025-08-29 Renamed water_nerf_gun file names
    [Bolt_Stand.stl, Desk_Stand.stl, Nerf_Nerf-N-Strike_Elite_HyperFire_Blaster_BOM.xlsx]
2025-09-02 Renamed Sound, movement and light folders and files
    [Base.stl, Base_Bottom_Cover.stl, Cable-Clamp.stl, Hasbro_Oink_Along_Songs_Peppa_BOM.csv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]
2025-09-02 Deleted dice roller files
    [Rumble Plate Base.stl, Rumble Plate Button.stl, Rumble Plate Cam.stl, Rumble Plate Lid.stl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]
2025-09-02 Edited file names
    [Cable-Clamp.stl, Cable_Tie_Holder_Back.stl, Cable_Tie_Holder_Front.stl, Gazillion_Tornado_Bubble_Machine_BOM.xlsx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]
2025-09-02 Updated file names
    [Nerf_Nerf-N-Strike_Elite_HyperFire_Blaster_BOM.xlsx]
2025-09-02 updated unavailable bubble toy file names
    [Playday_Bubble_Blower_Fan_BOM.csv, Playday_Bubble_Blower_Fan_BOM.xlsx]
2025-09-02 Renamed unavailable sound movement and light file names
    [FAO_Schwarz_3D_Light_Up_Spin_Art_BOM.xlsx, FAO_Schwarz_3D_Light_Up_Spin_Art_Maker_Guide_BOM.xlsx, Fisher-Price_Boppin_Beaver_BOM.xlsx, Fisher-Price_Cool_Beats_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]
2025-09-02 Changed headers to say "maker guide"
    [Base.stl, Base_Bottom_Cover.stl, Jack_Cover.stl, LightWand_Base_v1.2.stl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]
2025-09-04 Renamed 3D_Print_Files to 3D_Printing_Files
    [Base.stl, Base_Bottom_Cover.stl, Bolt_Stand.stl, Cable-Clamp.stl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]
2025-09-04 renamed my pal scout and violet files
    [Leapfrog_My_Pal_Scout_Violet_Solderless_BOM.xlsx]
2025-09-12 Uploaded monster Jam RC documents
    [Cable Clamp Back 2.stl, Cable Clamp Front 2.stl, Clamp v2 v11 v2.f3d]
2025-09-17 Renamed Monster truck file names
    [Cable Clamp Back 2.stl, Cable Clamp Front 2.stl, Clamp v2 v11 v2.f3d]
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2025-09-23 Uploaded a test version of the toy list
    [Toy_List_Test.csv]
2025-09-23 Updated a test version of the toy list
    [Toy_List_Test.csv]
2025-09-23 Removed the test toy list
    [Toy_List_Test.csv]
2025-09-23 3d print files in spinning light wand
    [Base.stl, Base_Bottom_Cover.stl, Jack_Cover.stl, LightWand_Base_v1.2.stl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]
2025-09-23 removed avaliable/unavaliable toy folders
    [Bolt_Stand.stl, Cable Clamp Back 2.stl, Cable Clamp Front 2.stl, Cable-Clamp.stl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]
2025-10-02 Added Dimple Peek a Boo Bunny and Elephant instructions and cable clamp STL
    [Dimple_Peep_a_Book_Elephant_Bunny_Cable_Clamp.stl]
2025-11-05 Added 3d print files for spinning light wand mono jack version
    [Base.stl, Base_Bottom_Cover.stl, Jack_Cover.stl]
2026-05-15 Added Zero Gravity RC Car Instructions
    [Cable_Clamp_Back.stl, Cable_Clamp_Front.stl, Clamp v2 v11 v2.f3d]
2026-06-16 Added Monster Jam RC Cars Instructions
    Added instructions for Monster Jam RC cars. This includes El Toro Loco, Megalodon, and Marvel Iron Man varieties.
    [Cable_Clamp_Back.stl, Cable_Clamp_Front.stl, Clamp v2 v11 v2.f3d]
2026-06-16 Monster Jam RC Car - rename folder
    [Cable_Clamp_Back.stl, Cable_Clamp_Front.stl, Clamp v2 v11 v2.f3d]
2026-06-25 Added XShot Motor Soaker Water Gun
    [Water Gun Stand - ZURU XSHOT Motor Soaker.f3z, Water_Gun_Stand_ZURU_XSHOT_Motor_Soaker.stl]
